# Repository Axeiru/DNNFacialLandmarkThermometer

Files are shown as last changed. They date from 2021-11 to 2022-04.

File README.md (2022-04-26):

# DNN Facial Landmark Thermometer
## GPU-Accelerated Facial Landmark Thermometer for Jetson Nano & PureThermal Mini using FLIR Radiometric Lepton 3.5
### This project attempts to detect fevers by tracking the medial canthus of the eye which serve as a proxy for internal body temperature.

<br/>

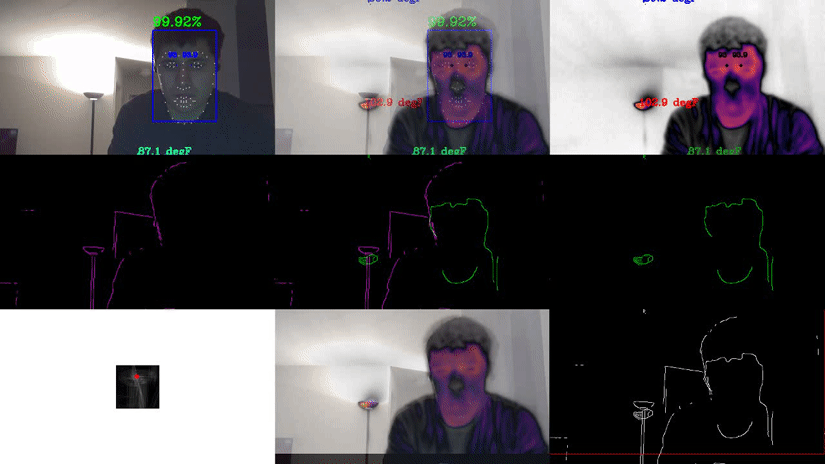
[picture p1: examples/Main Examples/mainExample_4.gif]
mainExample_4


### Parts List

| Item  | Approximate Price |
| ------------- | ------------- |
| Raspberry Pi Camera Module 2, [link.](https://www.raspberrypi.com/products/camera-module-v2/)  | $25.00  |
| FLIR Lepton 3.5, 160×120, 57° with shutter, Core Only, [link.](https://www.flir.com/products/lepton/?model=3.5+Lepton) [link.](https://groupgets.com/manufacturers/teledyne-flir/products/lepton-3-5) | $149.00  |
  | Jetson Nano Developer Kit, [link.](https://developer.nvidia.com/embedded/jetson-nano-developer-kit)  | ~$99  |
  | PureThermal Mini - FLIR Lepton Smart I/O Module, [link.](https://groupgets.com/manufacturers/getlab/products/purethermal-mini-flir-lepton-smart-i-o-module)  | $79.99  |
  | Arducam Sensor Extension Cable 300MM, [link.](https://www.arducam.com/product/b0186-arducam-imx219-sensor-extension-cable-raspberry-pi-nvidia-jetson-nano/)  | $12.99  |
  | NF-A4x20 5V PWM, [link.](https://noctua.at/en/nf-a4x20-5v-pwm)  | $25.00  |
  | SAMSUNG EVO Select Micro SD Card + Adapter - 64GB, [link.](https://www.amazon.com/dp/B09B1F9L52/) | $9.99 | 
  | Intel Dual Band Wireless-AC 8265 Desktop Kit, [link.](https://www.amazon.com/Intel-Wireless-Access-Point-8265-NGWMG-DTX1-Desktop/dp/B07666K4PZ) | ~$25 | 
  | Adafruit 5V 4A (4000mA) switching power supply - UL Listed, [link.](https://www.adafruit.com/product/1466) | $14.95 |
  | Cable Matters Combo-Pack Right Angle USB Cable, [link.](https://www.amazon.com/gp/product/B00S8GU03A/) | $7.99 |
  | Total: | **~$500** |

  | Alternate Solution(incomplete) | Approximate Price |
  | ------------- | ------------- |
| TELEDYNE FLIR BOSON 640 X 512, Core Only, [link.](https://www.flir.com/products/boson/)  [link.](https://www.oemcameras.com/flir-boson-640x480-24mm.htm)  | **~$3,520.00**  |
| Note: Requires additional supporting hardware. | |

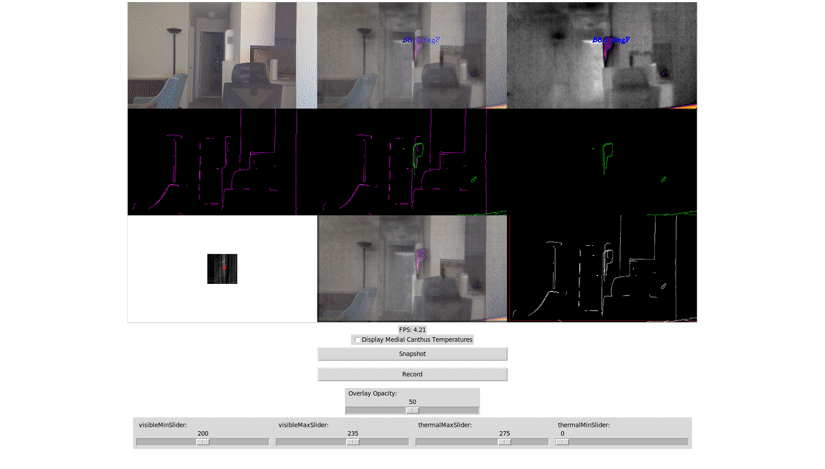
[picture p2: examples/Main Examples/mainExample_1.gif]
mainExample_1


<br/>

### Installation:

1. To begin, update your Jetson and install dependencies by running the following:
```
sudo apt update
sudo apt upgrade
sudo apt install python3-pip
pip3 install dlib
pip3 install Pillow
```
2. This project requires OpenCV to have CUDA compiled for GPU-acceleration, run the following:
```
git clone https://github.com/mdegans/nano_build_opencv.git
cd nano_build_opencv/
./build_opencv.sh
```
3. Finally to run:

```
git clone https://github.com/Axeiru/DNNFacialLandmarkThermometer.git
cd DNNFacialLandmarkThermometer/
python3 DNNFacialLandmarkThermometer.py
```

mainExample_2

### Working Principles:

Visible and thermal images contain radically different information that often do not correspond. This issue is side-stepped by performing Canny edge-detection and finding the (x,y) offsets between images which maximize 'similiarity' between detected edges. The images are aligned according to the coordinates of their maximum computed cross-correlation. 

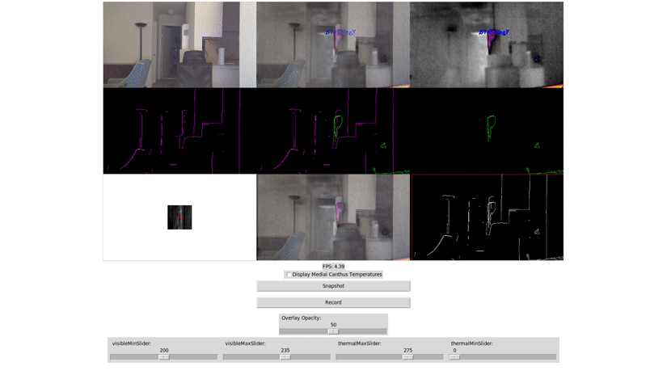
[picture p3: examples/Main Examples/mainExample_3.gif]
mainExample_3


### Usage:

- This program displays 9 views:
```
[[visibleImageDetectedFaces, overlayedView, thermal_image],
[visibleCanny, cannyOverlayedView, thermalCanny],
[crossCorrelationFrame, croppedOverlayedAligned, simulatedCroppedOverlayedCanny]]
 ```
- The medial canthus temperature of each detected face can be labelled in real time by toggling "Display Medial Canthus Temperatures"

- The displayed views can be saved as a video or as individal frames.

- Min/max temperatures are labelled on ```thermal_image```

- Spot temperature readings are labelled on ```visibleImageDetectedFaces``` and ```thermal_image``` at the mouse cursor's position

- The opacity of ```overlayedView``` and ```croppedOverlayedAligned``` can be controlled via the opacity slider.

- Canny edge-detection hysteresis thresholds can be controlled for each image via sliders.

- The background is normally white, however, it switches between:
  - Green, if faces are detected and all medial canthus temperatures are below the fever threshold of 38 degrees Celcius
  - Red, if a fever is detected, i.e. medial canthus temperature >= 38.0 Celcius.

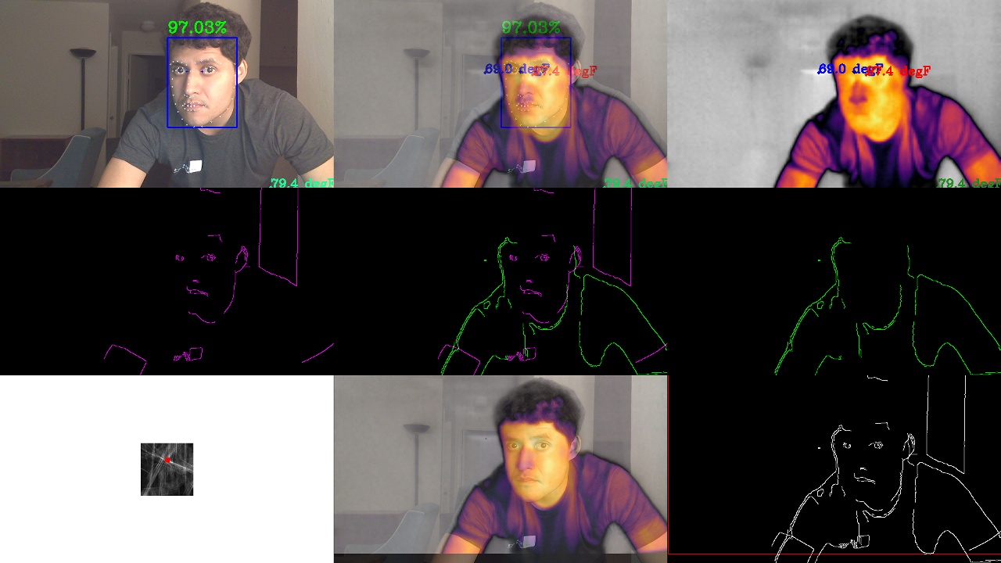
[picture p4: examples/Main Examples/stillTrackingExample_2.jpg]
stillTrackingExample_2


### Limitations & Future Avenues for Image Registration Improvement:

This implementation is entirely linear and naive. It does template-matching which is a simple sweep between images. It cannot account for the non-linear distortion present in optical lenses. Furthermore, it only applies image offsets and is less expressive than an affine transformation as no rotation or scaling is attempted. Ideally a non-linear projection between captured images would be used.

Currently, this implementation naively chooses the coordinates of maximum similarity, when better heuristics may exist:

- A neural-based [Deep Image Homography Estimation](https://arxiv.org/pdf/1606.03798.pdf) model may be particularly effective

- A monocular depth estimation model may be used in tandem with a semantic segmentation model to non-linearly deform the images to match

- A momentum-based point model could be used to prevent discontinuitues in image offsets, ensuring smooth adjustments

- Another possibility is applying a Gaussian mask to the computed cross-correlation to prefer smaller, more central offsets.

### General Notes:

- Overclocking is recommended to attain maximum performance, however, this requires recompiling the kernel and takes several hours. A procedure to overclock the Jetson Nano's CPU to 2GHz & GPU to 1.2GHz will be added.

- This project was entirely developed on a Jetson Nano, including recording & transcoding examples.

- This project is built upon the stock Jetson Nano 4GB Developer Kit SD Card Image (JetPack 4.6) released by NVIDIA. Apart from building OpenCV from source for CUDA support, all dependencies are included in the stock image.

- Future offloading of image processing to the Jetson's GPU and the STM32F412 microprocessor in the PureThermal Mini should generally improve performance

- A Jetson Nano 4GB is highly recommended as the facial detection model and matrix operations consume ~1GB of RAM. This project may run on the Jetson Nano 2GB, but this hasn't been tested yet and may result in severe memory thrashing.

#### Framerate-specific Notes:

- Ideally, images would be captured from each camera in separate threads, however, tkinter is inherently single-threaded. Future revisions may move away from tkinter to implement proper multithreaded image capture.

- The FLIR Lepton 3.5's maximum capture rate is ~9Hz which presents an artifical 'sweet-spot,' though higher visible framerates still appear smoother. A Jetson Xavier NX is likely better suited at running the current implementation at useable framerates than a Jetson Nano.

- Presently the most computationally intensive operations performed are Canny edge-detection and the cross-correlation template matching. The most direct way to improve performance is by reducing ```self.alignment_padding``` to smaller values. This will have the effect of reducing the maximum possible offset.

### Planned improvements/features:

- Manually setting high-gain mode & skin emissivity values via firmware
- Implementing command line options
- Custom colormaps, resolutions, views
- Logging to file(# of detected faces, temperatures, general statistics, etc.)

example_3

### Supporting Resources:

*Multispectral Thermal Imaging with a LWIR+VIS Camera*

- Hines, Jacob, and Evan Wang. “Multispectral Thermal Imaging with a LWIR+VIS Camera.” *Stanford EE367 / CS448I: Computational Imaging*, Stanford University, 17 Mar. 2019, http://stanford.edu/class/ee367/Winter2019/hines_wang_report.pdf.

  - Extremely illuminating and informative survey into multispectral image registration and fusion. Many thanks to the Authors!
  
Access to a 3D printer is recommended but not necessary. The [Jetson NanoBoxABS for B01](https://www.thingiverse.com/thing:4275167) is a nice case that I can recommend.

The included stl can be printed to serve as an alignment mount for the FLIR Lepton & Raspberry Pi Camera Module:

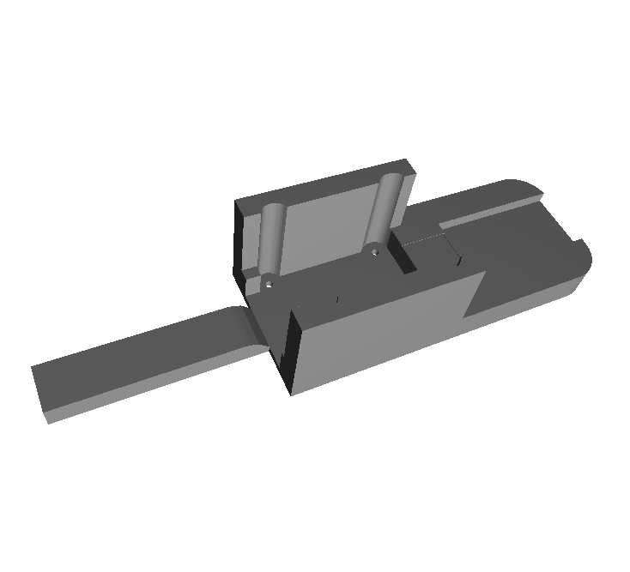
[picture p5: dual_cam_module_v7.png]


- Copies of required files are included, however, original sources are listed below and deserve many thanks!
  - deploy.prototxt.txt: [source.](https://github.com/keyurr2/face-detection/blob/master/deploy.prototxt.txt) - MIT License

  - res10_300x300_ssd_iter_140000.caffemodel: [source.](https://github.com/keyurr2/face-detection/blob/master/res10_300x300_ssd_iter_140000.caffemodel) - MIT License

  - shape_predictor_68_face_landmarks.dat: [source.](https://github.com/davisking/dlib-models/blob/master/shape_predictor_68_face_landmarks.dat.bz2) - Creative Commons Zero v1.0

### More Examples:
#### Samples are also provided in original resolution
example_1

example_2

startupExample

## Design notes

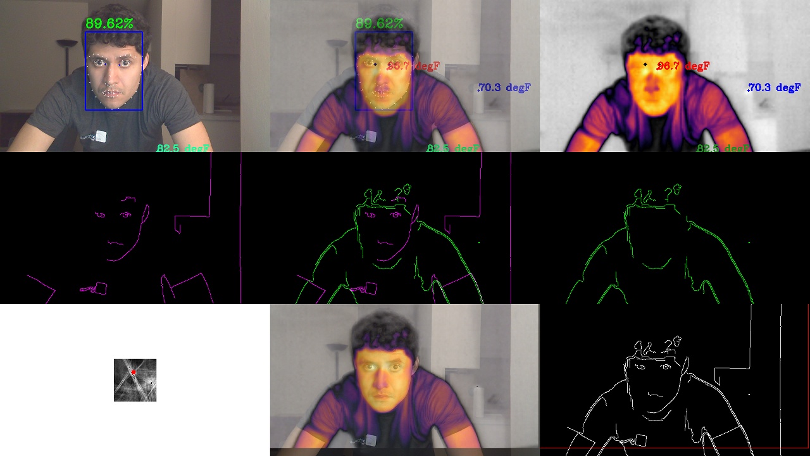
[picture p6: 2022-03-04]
examples/Main Examples/stillTrackingExample_3.jpg

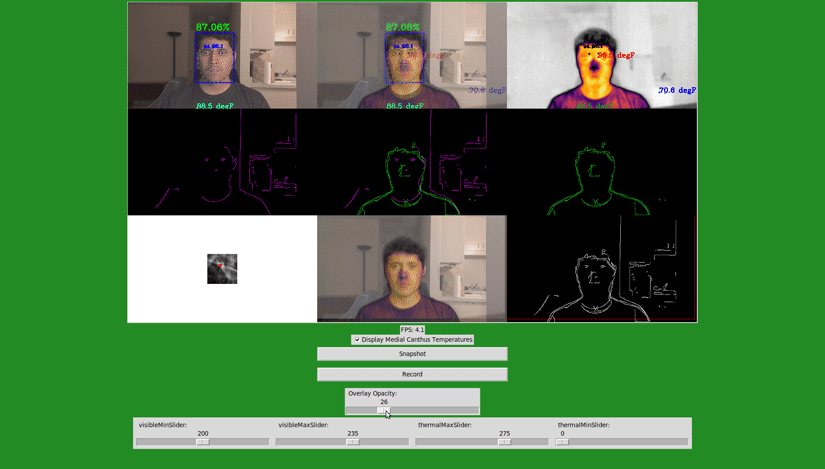
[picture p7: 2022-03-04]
examples/Main Examples/opacityExample.gif

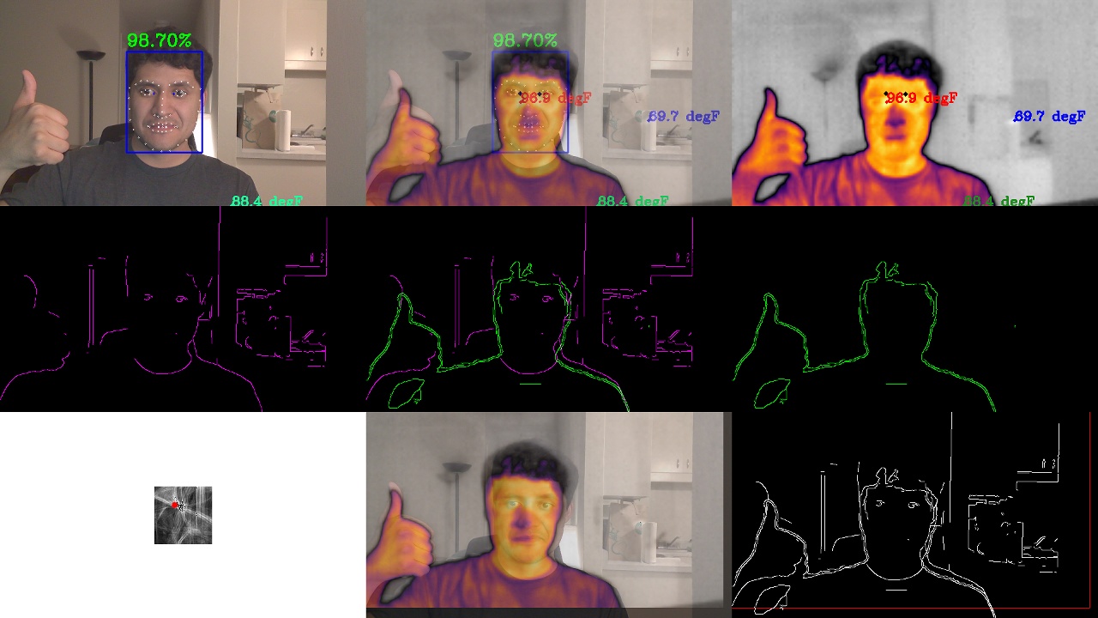
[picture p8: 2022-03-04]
examples/Main Examples/stillTrackingExample_1.jpg

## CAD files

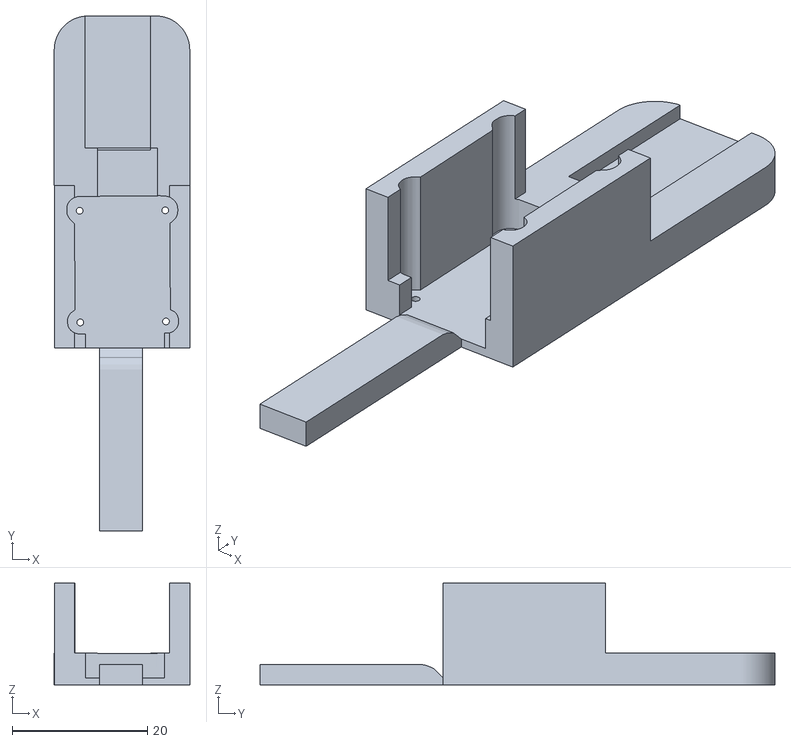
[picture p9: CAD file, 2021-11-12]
dual_cam_module_v7.stl
20.0 x 76.1 x 15.0

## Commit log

2021-11-12 added dual camera module 3d model
    [dual_cam_module_v7.stl]
2022-03-04 Tuned parameters to improve framerate & accuracy, also fixed missing canny overlay
2022-03-04 Updated video recording framerate
